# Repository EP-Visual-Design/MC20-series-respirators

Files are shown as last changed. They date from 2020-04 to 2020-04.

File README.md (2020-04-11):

# MC20 Series 3D Printable Respirator



These designs are free to download and print for use.

Contact us (contact@epvisual.com) to request use of our two available 3-D printers.

**Note**: Unlike N95 respirators, our respirator designs are not evaluated, tested, and approved by the National Institute for Occupational Safety and Health (NIOSH) as per the requirements in 42 CFR Part 84.

## Background

An N95 respiratory protective device is designed to achieve a very close facial fit and very efficient filtration of airborne particles. These respirators are fluid resistant, disposable, and currently used in hospitals to protect staff from coronavirus. Non-disposable, rated respirators with replaceable filters are a better option; but they are hard to clean, expensive, proprietary, and the filters are not readily available.

Because the N95 respirator is more expensive and supplies are low, hospital staff are often using the disposable, loose-fitting surgical face masks as an alternative. Though these are designed to be thrown away after one use, hospital staff are often reusing them due to the low supplies of personal protective equipment (PPE). These masks are not designed to form a seal around the nose and mouth, and all disposable masks are easily damaged when attempting to wash and reuse.

## The Current Situation

### Availability

N95 respirators are not readily available and, if available, are expensive.

### Level of Protection

Disposable masks do not provide the same level of protection. Loose-fitting disposable surgical masks are not designed to form a seal around the nose and mouth.

### Possible Reuse

Disposable masks are not meant for reuse. You cannot properly clean disposable masks without risking damage to layers of the mask.

In response to this pandemic of the 2019 novel coronavirus, COVID-19, many individuals and companies are contributing resources and services in ways that they are able.

As a company with 3-D design and printing capabilities, we want to contribute our designs to create PPE that may be useful in keeping hospital staff safe as they care for sick patients and battle the coronavirus.

Our hope with this open source project is to provide a:

* Usable respirator that can be printed now to fill current availability gaps
* Sturdier, safer option than homemade fabric masks
* Two-piece respirator that is easy to clean with disposable padding and filters
* Product that can be tested, peer reviewed, and refined by experts in the field

## Our Solution

### Share

EP Visual wants to share and allow for free use of our respirator designs in an open source platform. We want to encourage further development and get additional user feedback.

### Protect

Our respirator designs are made to incorporate any approved filter media that can be made to fit the two sizes. We have experimented with a cotton layer, activated carbon layer, and MERV 14 layer with comfortable breathing and have achieved what seems like a good seal.

### Reuse

Our solid designs are made for reuse. Nooks and crannies are minimized, and polycarbonate printing filament is both chemical, water, and heat resistant. The reusable padding/seals can be customized, removed, and easily replaced.

**Note:** Unlike N95 respirators, our respirator designs are not evaluated, tested, and approved by the National Institute for Occupational Safety and Health (NIOSH) as per the requirements in 42 CFR Part 84.

## MC2055

### 55mm filter media

* **MC2055NS**: Supports a 55mm diameter X 5mm filter. Slimmer design, smaller, prints fastest.
* **MC2055NS-K**: MC2055NS - scaled to 80% for kids.

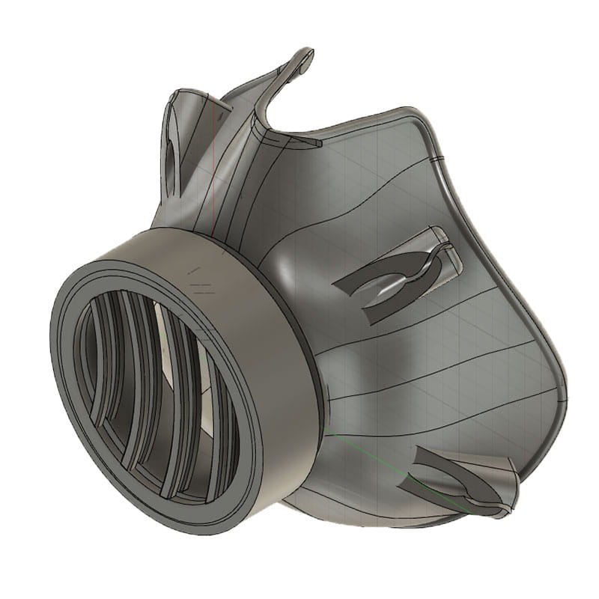
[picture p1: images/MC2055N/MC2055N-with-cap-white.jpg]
MC2055N with cap


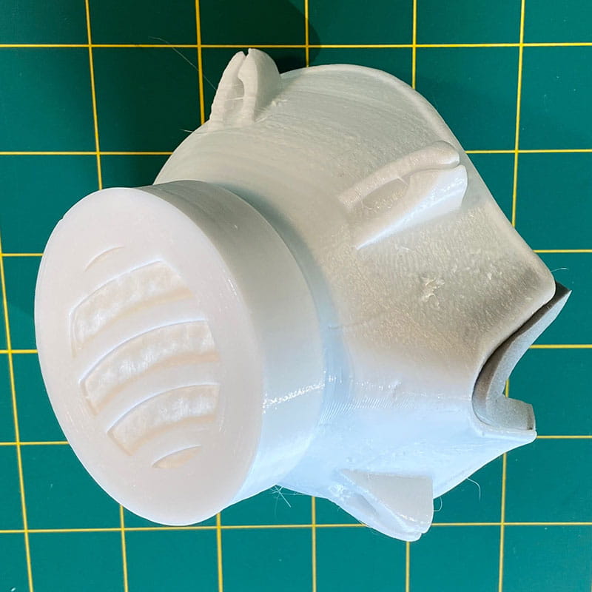
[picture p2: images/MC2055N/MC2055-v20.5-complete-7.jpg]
finalized MC2055N with cap print


Additional images available in the images directory.

## MC2080

### 80mm filter media

* **MC2080N2SP**: Supports an 80mm diameter X 5mm thick round filter. Slimmer design, smaller, prints faster.
* **MC2080N2SP-H**: MC2080NS that includes a hydration portal and storage for a 7mm, medical grade silicone tube.

**Note**: The MC2080N2SP-H.f3d Fusion 360 files contains both the _N2SP_ and _N2SP-H_ models.

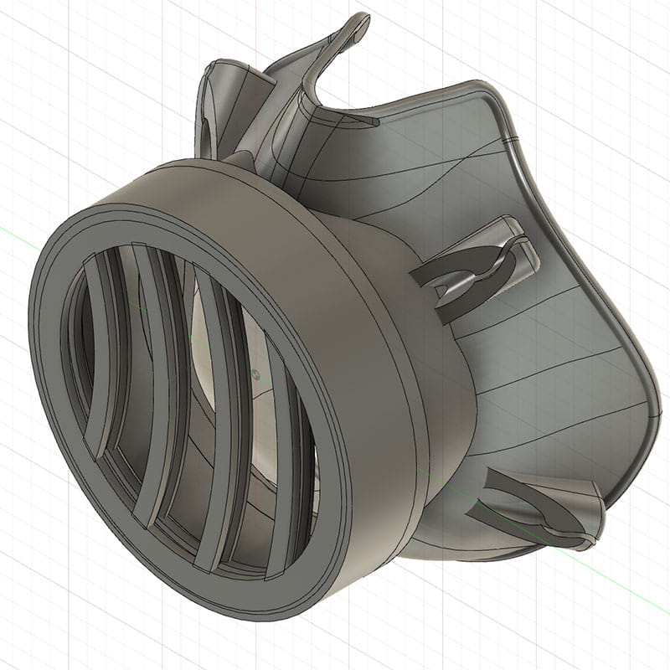
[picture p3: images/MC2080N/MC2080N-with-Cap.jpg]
MC2080N with cap render


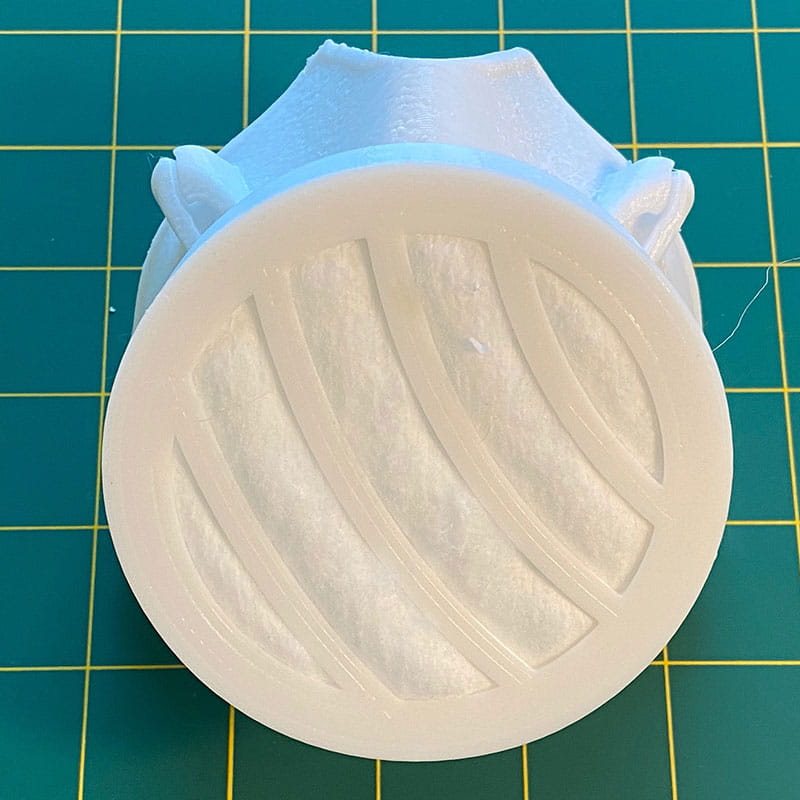
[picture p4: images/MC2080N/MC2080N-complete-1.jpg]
MC2080N with cap final print


Additional images available in the images directory.

## Additional Information

We have printed these respirators out of polycarbonate with flexible filter options. Currently we are experimenting with a multi-layer filter. The first layer is made of a cotton disk and the second layer is made with Merv 14 filter media. Both layers are cut into 55mm and 80mm circles. We have also added an activated carbon filter layer which produces comfortable breathing results. For the seal around the nose area, we have trialed both a silicone gasket and foam tape. The seal, along with filter material, is designed to be thrown away before sterilizing. Though not officially evaluated by an authoritative source, we believe these respirators work better than the fabric masks because there is a more effective seal around the nose and mouth.

With further testing, we hope to find a way to make it easier to secure the filter media without any gaps. We tested options with removable grids, but ultimately decided that additional parts may create risks with cleaning and the potential for missing pieces. As part of our experimentation with the respirator, we developed a secondary, internal filter cartridge, but were not able to consistently get it to seal, which resulted in making cleaning difficult.

Future product improvement opportunities:

* Develop filter standards and work with filter makers to produce a non-proprietary replacement filter
* Create a version for general use that is lightweight, subtle, and more comfortable for everyday wear
* Create child-size versions

## Cleaning/Care

Our masks are designed to be easy to clean.

Because the coronavirus lives on plastic for three days, the respirators need to be disinfected after each use with bleach or alcohol. Ultimaker polycarbonate and Polymaker POLYMAX PC are both heat and chemical resistant and don’t absorb water. We have read on some Autoclave manufacturers websites that polycarbonate can be disinfected in a standard Autoclave, but we have not tested this with these printed respirators. If printed in polycarbonate, DO NOT use alkaline cleaners like ammonia or lye.

## Printing Specifications

### Materials Used

* Polymaker PolyMax PC – White
* Ultimaker White PC

### Printers Used

* Ultimaker S5
* Ultimaker S3

### Printer Details

* Print Nozzle used: Ultimaker 0.8mm
* Most settings: Default for material
* Layer heights tested: 0.2mm, 0.3mm, 0.4mm
* Infill: 100% (limit the gaps in the respirator print)
* Support: OFF (with the surface area of the model and the adhesion bodies included in the model, we have had success with no support)
* Build Plate Adhesion: OFF

## Resources

* [FDA N95 Respirators and Surgical Masks (Face Masks)](https://www.fda.gov/medical-devices/personal-protective-equipment-infection-control/n95-respirators-and-surgical-masks-face-masks)
* [CDC Strategies for Optimizing the Supply of N95 Respirators: Crisis/Alternate Strategies](https://www.cdc.gov/coronavirus/2019-ncov/hcp/respirators-strategy/crisis-alternate-strategies.html)
* [CDC: Understanding the Difference - Surgical Mask vs. N95 Respirator](https://www.cdc.gov/niosh/npptl/pdfs/UnderstandDifferenceInfographic-508.pdf)

### Where to Find Supplies

#### Straps (Any elastic material can work)

* [Grifiti Band Joes X Cross Style 12" Assorted Color 10 Pack Cooking Grade, Pressure Cooker, Crock Pot, Puzzles, Board Games Heat Cold UV Chemical Resistant Silicone Rubber by Grifiti](https://www.amazon.com/dp/B00GLJ421W/ref=cm_sw_em_r_mt_dp_U_HhZHEb0QJJ882)
* [Coopay Large Heavy Duty Latex Rubber Bands Trash Can Bands for Office Supply, File Folders, Cat Litter Box, Size 12 inches, 30 Pack (White) by Coopay US](https://www.amazon.com/dp/B07VNC7X93/ref=cm_sw_em_r_mt_dp_U_xiZHEbRNAAG2Z)

#### Seal and comfort tape as needed

* [Nexcare Absolute Waterproof Tape, Hypoallergenic, 1 Inch x 5 Yard Roll, 6 Rolls by Amazon.com](https://www.amazon.com/dp/B07GSQJH19/ref=cm_sw_em_r_mt_dp_U_YvZHEbYSG2HSN)
* [3M 2770-2 Kind Removal Silicone Tape (Pack of 6) by Simply Prime](https://www.amazon.com/dp/B00KHVWXWA/ref=cm_sw_em_r_mt_dp_U_JxZHEbH61C4V0)

#### Tubing For MC2080NS-H Model

* [Pure Silicone Tubing - 1/8" ID x 1/4" OD - High Temp Kink-Free Hose Tube 500F (20 Feet)
by Cold & Colder](https://www.amazon.com/dp/B07V5T2ZY1/ref=cm_sw_em_r_mt_dp_U_VFHJEbFDA5BSM)

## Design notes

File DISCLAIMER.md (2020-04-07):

# MC20 Series Respirator Open Source Prototype Project

Thank you for requesting a sample of our respirator and for your interest in our open source project. Our hope is to provide a necessary product at a time when it is in demand and to further improve this product by welcoming feedback. We encourage public contribution of ideas and expertise in order to create an open source standard that can be evaluated and approved.

## Disclaimer

**Note**: Unlike N95 rated respirators, our designs are not evaluated, tested, and approved by the National Institute for Occupational Safety and Health (NIOSH) as per the requirements in 42 CFR Part 84.

THIS PRODUCT IS PROVIDED "AS IS"  WITH NO WARRANTIES OF ANY KIND, EITHER EXPRESS, IMPLIED, OR STATUTORY.   SELLER SPECIFICALLY DISCLAIMS ANY IMPLIED WARRANTIES OF  TITLE, MERCHANTABILITY, FITNESS FOR A PARTICULAR PURPOSE AND  INFRINGEMENT. THE EXCLUSIVE REMEDY AGAINST SELLER FOR ANY CAUSE OF  ACTION RELATING TO THE HANDLING OR USE OF THE PRODUCTS SOLD BY  SELLER IS A CLAIM FOR DAMAGES AND IN NO EVENT SHALL DAMAGES OR ANY OTHER  RECOVERY OF ANY KIND AGAINST SELLER EXCEED THE PRICE OF THE SPECIFIC  PRODUCTS WHICH CAUSED THE ALLEGED LOSS, DAMAGE, INJURY, OR OTHER CLAIM.   SELLER SHALL NOT BE LIABLE FOR, AND ANY AND ALL CLAIMS AGAINST SELLER  ARE WAIVED FOR, SPECIAL, INDIRECT, INCIDENTAL, OR CONSEQUENTIAL DAMAGES  OR EXPENSES OF ANY NATURE, INCLUDING BUT NOT LIMITED TO: LOSS OF PROFITS  OR INCOME, AND PROPERTY LOSS OR DAMAGE, WHETHER OR NOT BASED ON  SELLER’S NEGLIGENCE, BREACH OF WARRANTY, STRICT LIABILITY IN TORT OR ANY  OTHER CAUSE OF ACTION. THIS WARRANTY GIVES YOU SPECIFIC LEGAL RIGHTS, AND YOU MAY HAVE ADDITIONAL RIGHTS WHICH VARY FROM STATE TO STATE.

## Notes

We are still working on improving both the filter and filter replacement method. We have inquired about a manufactured filter that will meet desired standards and be easier to replace. An open source 55mm and 80mm round filter would be a generic design that could be made by any manufacturer and fit in any respirator that supports such a standard. Currently, the respirator cap has to be tightened carefully to avoid wrinkling the filter material. It is possible a future design would not need the retaining grid on the filter body if the filter was able to retain its shape without it.

These respirator caps and bodies were printed with Polymax PC, Polylite CC, or Ultimaker PC. We would expect that all tape, padding, and filter material be thrown away after each use. The polycarbonate can be cleaned with soap and water, hot water, chlorine-based cleaners, or alcohol. Do not use a high-PH cleaner like lye or ammonia. Whatever cleaner is used, it is important to make sure the cleaner is safe for humans. In addition, the polycarbonate must be properly rinsed.

Send any comments or suggestions to contact@epvisual.com.

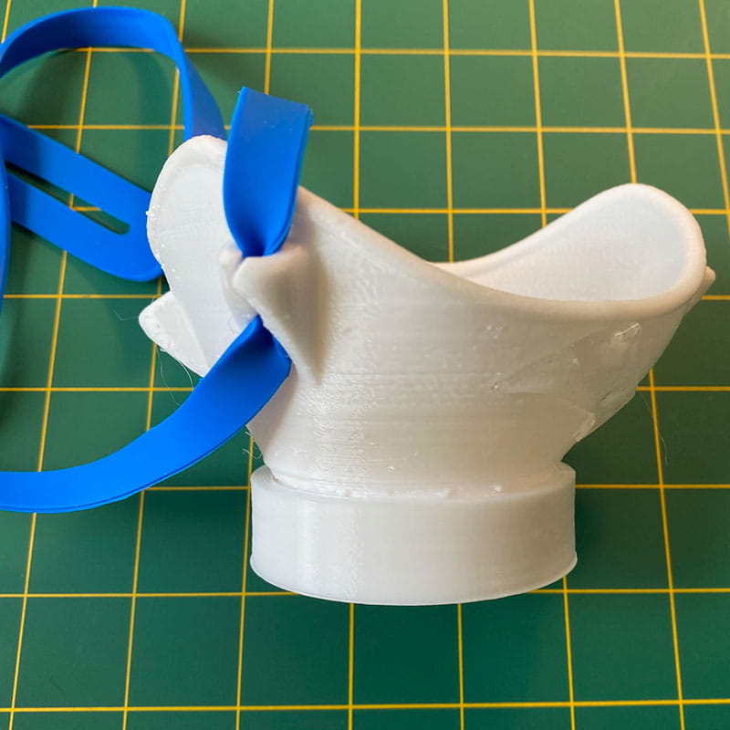
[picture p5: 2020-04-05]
images/MC20R/MC20R-strap-2.jpg

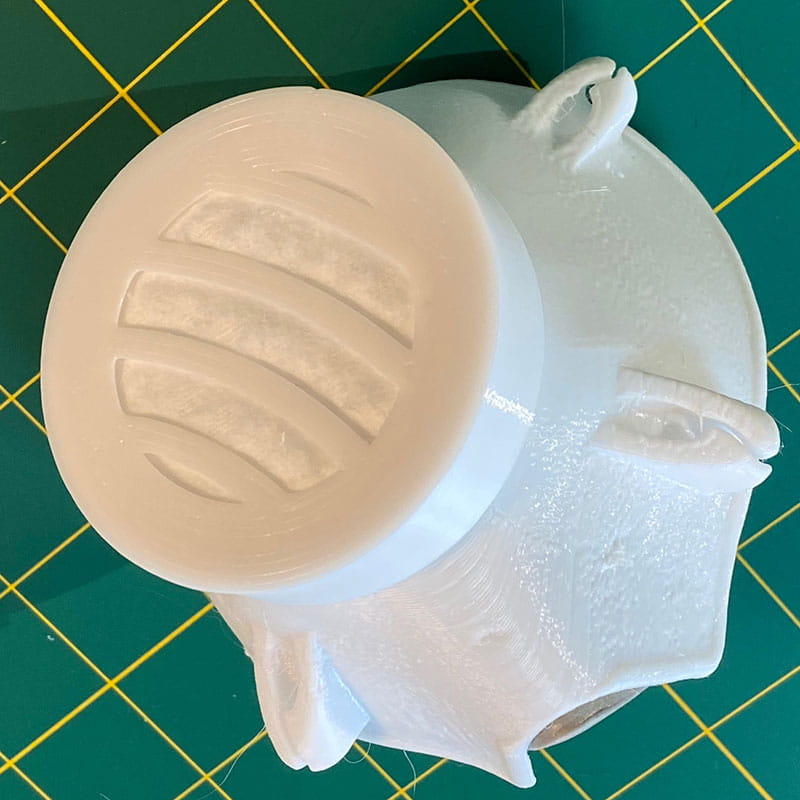
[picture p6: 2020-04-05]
images/MC2055N/MC2055-v20.5-complete-5.jpg

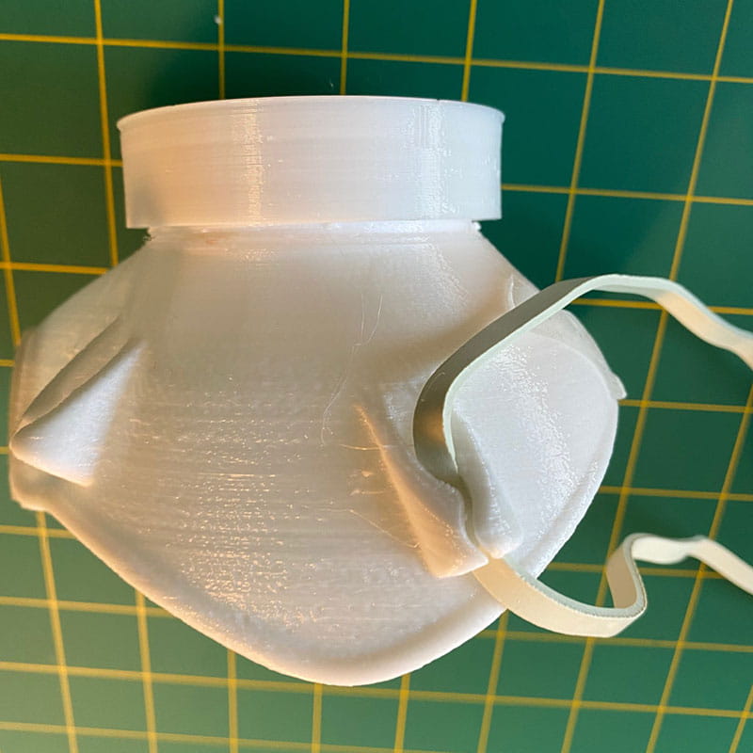
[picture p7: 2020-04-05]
images/MC20R/MC20R-strap-4.jpg

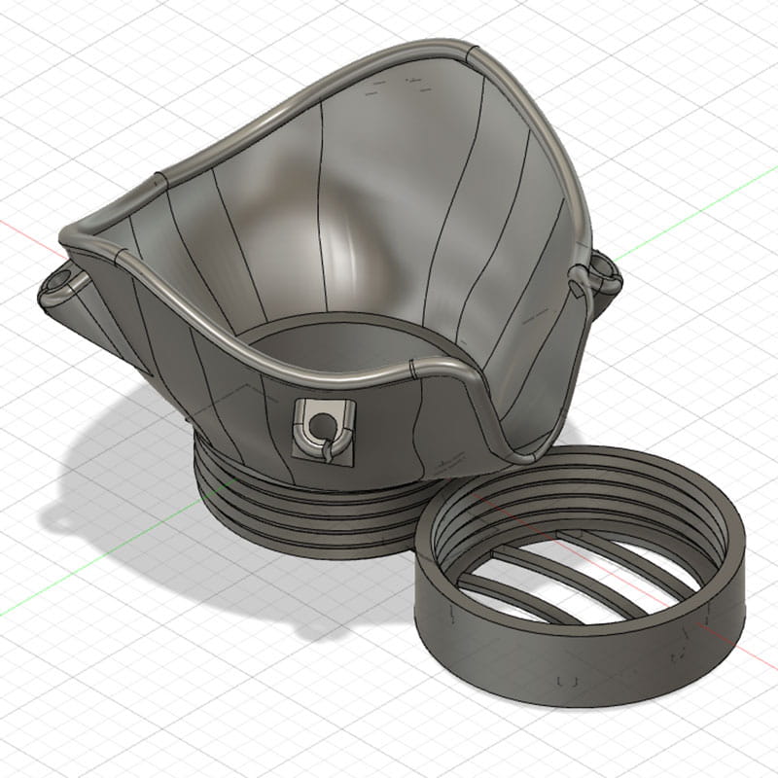
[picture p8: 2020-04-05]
images/MC2055N/MC2055N-V20.5-flat.jpg

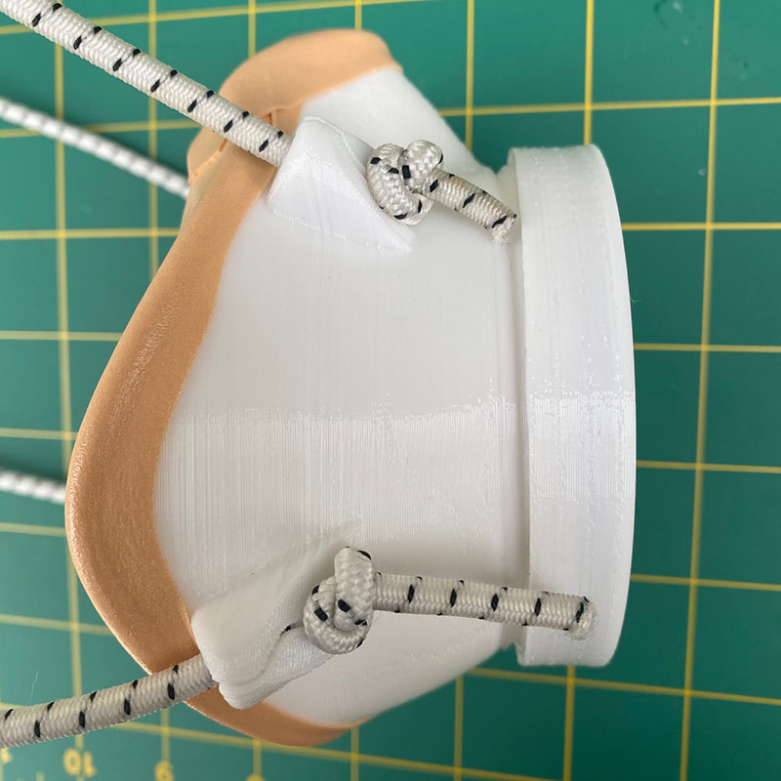
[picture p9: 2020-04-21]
images/straps/bungee-002.jpg

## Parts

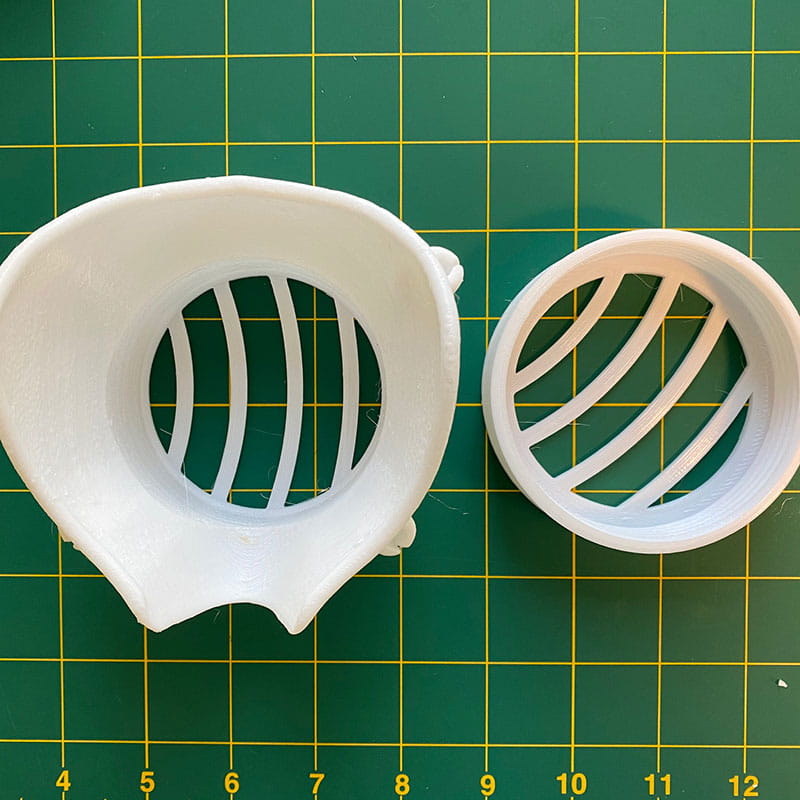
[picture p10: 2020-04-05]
images/mask-parts/example-3.jpg

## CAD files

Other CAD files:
stl/MC2055/MC2055NS-K.stl
stl/MC2080/MC2080N2SP.stl
stl/MC2055/MC2055NS.stl
stl/MC2080/MC2080N2SP-H.stl
Fusion-360/MC2055/MC2055NS.f3d
Fusion-360/MC2080/MC2080N2SP-H.f3d

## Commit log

2020-04-05 🚀 Deploy MC20 Template Files
    [MC2055N.f3d, MC2055N.stl, MC2055NS.f3d, MC2055NS.stl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]
2020-04-05 📦 Add Master Template Download
    [MC2055N.f3d, MC2055NS.f3d, MC2080N.f3d, MC2080NS.f3d]
2020-04-06 ✏️ Update README
2020-04-06 🏗️ UpdateMC2055NS STL File
    [MC2055NS.stl]
2020-04-07 🚚 Add MC2055NS-K & MC2080NS-H STL Files
    [MC2055N.f3d, MC2055N.stl, MC2055NS-K.stl, MC2055NS.f3d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]
2020-04-07 📄 Add Product Disclaimer
2020-04-09 🍱 Add MC2080NS-H Fusion 360 File
    [MC2080NS-H.f3d]
2020-04-11 🏗️Update MC2080 Files
    [MC2055N.f3d, MC2055N.stl, MC2080N.f3d, MC2080N.stl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]
2020-04-21 🖼️ Add MC20Straps Images
